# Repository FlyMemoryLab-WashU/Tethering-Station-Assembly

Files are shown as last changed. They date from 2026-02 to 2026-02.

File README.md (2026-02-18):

# Instructions for building the inexpensive tethering station
---
<div align="center">
  
    <p><strong>Figure 1:</strong> Fly tethering station.</p>
</div>

### Table of Contents
- [1. Prepare all needed parts](#1-prepare-all-needed-parts)
- [2. Assemble the acrylic frame](#2-assemble-the-acrylic-frame)
- [3. Assemble the peltier cooler](#3-assemble-the-peltier-cooler)
- [4. Mount the micromanipulator](#4-mount-the-micromanipulator)
- [5. Install the thread adapter and Mini-V clamp](#5-install-the-thread-adapter-and-mini-v-clamp)
- [6. Install the fly-holding rod and fly holder](#6-install-the-fly-holding-rod-and-fly-holder)
- [7. Power on and set the cooler temperature](#7-power-on-and-set-the-cooler-temperature)
- [8. Required parts list](#8-required-parts-list)
  
## Assembly Steps

### 1 Prepare all needed parts

#### 1.1 Verify purchasable items
- Confirm you have all **purchasable components** listed in the **Required Parts List (PPL)** table.
- Purchase any missing items before starting the build.

#### 1.2 Prepare custom acrylic parts
- You need to prepare:
  - a. Acrylic fly holder.
   <div align="center">
    
    <p><strong>Figure 2:</strong> Acrylic fly mount, 1.5mm (1/16”) thickness.</p>
    </div>
    
  - b. Acrylic assembly for the tethering station.
    <div align="center">
        
    <p><strong>Figure 3:</strong> CAD rendering of the tethering station's acrylic assembly, designed in FreeCAD.</p>
    </div>
  
- Obtain these acrylic-sheet parts by either:
  - Laser-cutting the acrylic sheets yourself, or
  - Ordering laser-cut parts from a service (e.g., Ponoko).
- Check acrylic thickness before cutting/ordering. The SVG filenames indicate the required thickness:
  - **1.5 mm (1/16")**
  - **6 mm (1/4")**
- Cut paths only: all paths in the SVG files are intended to be **cut**, not engraved.
  - [Download fly holder SVG files](Fly_holder_1point5mm.zip)
  - [Download tethering station SVG files](Tethering-Station-v3.2.zip)
      
#### 1.3 Tap threads in the baseplate
- Tap **M3 threads** into the baseplate holes used to mount the micromanipulator.

#### 1.4 Prepare 3D-printed parts
- Obtain the 3D-printed parts by either:
  - Printing them yourself, or
  - Ordering them from a service (e.g., Craftcloud).
- Recommended filament:
  - **PLA** (works well for most uses)
  - **ASA** (recommended if you need improved UV resistance)
- Suggested print settings:
  - **0.2 mm layer height**
  - **No supports**
- Mini-V clamp: insert **M3 nuts** into both slots.

---

### 2 Assemble the acrylic frame
- Assemble the main structure using the acrylic parts, following the render in **Figure 3**.
- Fasten all acrylic joints with **cyanoacrylate adhesive** (super glue), as shown in **Figure 3**.

#### Optional: add rubber feet
For a better grip between the baseplate and the table, attach **four rubber feet** under the baseplate—**one at each corner**.

---

### 3 Assemble the peltier cooler

#### 3.1 W1209 temperature controller    
-   <div align="center">
       
    <p><strong>Figure 4:</strong> HiLetgo 2pcs W1209 with Case 12V DC Digital Temperature Controller.</p>
    </div>
    
- Assemble the **W1209 temperature controller (PPL)**.
- If your unit includes an acrylic housing, assemble the housing first.

> **Wiring safety note**
>
> Do **not** splice wires by twisting metal-on-metal only. Poor splices can overheat under load.
> Use one of the following:
> - solder + heat-shrink, or
> - proper connectors (e.g., crimp connectors or WAGO lever nuts).

#### 3.2 Wire the temperature controller to the peltier cooler
Prepare:
- one **3" red wire** (cut + strip ends)
- one **10" black wire** (cut + strip ends)
- **12 V power supply**
- **female barrel connector**
- **rocker switch**
- **Peltier cooloer**    
    <div align="center">
    
    <p><strong>Figure 5:</strong> Thermoelectric, Peltier Assemblies.</p>
    </div>

Wire as follows:
a. Use the **3" red wire** to connect terminals **K1 → 12V** on the W1209.
b. Connect one end of the **10" black wire** to **GND** on the W1209.
c. Connect the other end of the **10" black wire** to the **negative (−)** terminal of the **female barrel connector**.
d. Connect the **black wire** of the **rocker switch** to **12V** on the W1209.
e. Connect the **red wire** of the **rocker switch** to the **positive (+)** terminal of the **female barrel connector**.

**Cooler load wiring (Peltier + fan assembly):**
- **Red wires → K0**
- **Black wires → GND**

You can wire the cooler load either **now** or **after** mounting the cooler to the acrylic structure.

#### 3.3 Prepare and mount the aluminum T-bar
a. Cut a **40-mm-length** piece of the **aluminum T-bar** (a bandsaw works well).
b. Apply **thermal paste** to the bottom face of the T-bar (orientation as in **Figure 1**).
c. Place the **NTC temperature probe** so it touches **both**:
   - the rim of the T-bar, and
   - the cold plate  
   Add thermal paste to thermally couple the probe to both surfaces.
d. Secure the T-bar using **thermal tape** (use **4 × 10 mm** strips) as shown in **Figure 6**.
   
   - You do **not** need to remove the blue liner from the tape after applying it.

-   <div align="center">
    
    <p><strong>Figure 6:</strong> The aluminum T-bar on the cooler</p>
    </div>

#### 3.4 Seat the cooler on the acrylic frame
- Place the cooler into its seat as shown in **Figure 1**.
- Optionally use **cyanoacrylate adhesive** (super glue) for additional fastening.

---

### 4 Mount the micromanipulator
a. Place the micromanipulator on the acrylic baseplate **with the 6 mm raising platform underneath**.
b. To access the screw mounts:
   - Slide the lowest platform to an **edge position** to expose the screw holes on the opposite side.
c. Insert **M3 × 12** screws and fasten the micromanipulator into the baseplate.
d. Move the platform to the other edge position and repeat to install the remaining screws.

---

### 5 Install the thread adapter and Mini-V clamp

a. Screw your chosen **thread adapter** into the top surface of the micromanipulator.
b. Wrap **one layer** of **PTFE (thread seal) tape** or **electrical tape** around the exposed threads to add friction (prevents the clamp from rotating freely).
c. Attach the **Mini-V clamp** above the thread adapter.

#### Notes by clamp version

**3D-printed version (shown in Figure 1)**
- The “thread adapter” is an **M3 × 36** threaded rod.
  - We made this by cutting an **M3 × 40** screw down to **36 mm** using a rotary tool + cutoff wheel (other methods are fine).
- Fasten the rod by:
  a. threading it into the micromanipulator platform hole closest to the T-bar, then
  b. adding a **washer + nut** to lock it in place.

**Thorlabs-parts version**
- You may need **M3 standoffs** to reach the height of the aluminum T-bar apex.
- This was not tested; an M3 standoff kit is included in the PPL as an option.

---

### 6 Install the fly-holding rod and fly holder
a. Insert the appropriate **thumb screw** into the top of the Mini-V clamp (type depends on your clamp choice).
b. Insert the **fly-holding rod** (Thorlabs or 3D-printed) into the Mini-V clamp and secure it with the thumb screw.
c. Attach the acrylic fly holder to the rod using one of the following:
   - **M2.5 screw + nut**, or
   - **#2-56 screw + nut**
d. Use the small hole at one end of the fly-holding rod for the fly holder fastener.

---

### 7 Power on and set the cooler temperature

a. Plug the **12 V power supply** into the **female barrel connector**.
b. Turn on the **rocker switch** when you are ready to cool.

#### Recommended temperature setpoint
- Target: keep the **cold plate ~0 °C**.
- The NTC probe may not report the cold-plate temperature accurately.
- Using an IR camera, we found that setting the controller to **+10 °C** produced the desired cold-plate temperature (~0 °C).

#### How to set the temperature on the W1209
a. **Click** (do not long-press) the **SET** button, which will make the display flash.
b. Use **+** and **−** to adjust the set temperature.
c. Click the SET button again to set the displayed temperature.

## 8 Required parts list

| Name | Quantity | Description | Notes | Link |
|------|----------|-------------|-------|------|
| Tap Wrench Tool Set | 1 | Mesee 6 Pcs Tap Wrench Tool Set, Adjustable T-Handle Tap Holder Wrench with Metric Plug Taps (M3–M8) | | [Amazon](https://a.co/d/hpTYyof) |
| Super Glue | 1 | Loctite Super Glue Professional Liquid, 20 g | | [Amazon](https://a.co/d/eSluuwc) |
| Temperature Controller | 1 | HiLetgo W1209 (12V) Digital Temperature Controller (with case) | | [Amazon](https://a.co/d/bQPwmGg) |
| WAGO Lever Splice | 5 | Push-in butt splice connector, 12–24 AWG, transparent/orange | | [DigiKey](https://www.digikey.com/short/qq5hc085) |
| Black Wire | 1 | 22 AWG hook-up wire, black, 25 ft (7.62 m) | | [DigiKey](https://www.digikey.com/short/qm3t1whb) |
| Red Wire | 1 | 22 AWG hook-up wire, red, 25 ft (7.62 m) | | [DigiKey](https://www.digikey.com/short/whnmh5cv) |
| Rocker Switch | 1 | Rocker switch, SPST, 20A (AC) 125V, panel mount, snap-in | | [DigiKey](https://www.digikey.com/short/8pzjtrjv) |
| Thermal Tape | 1 | Double-sided thermal adhesive tape, 25 m × 10 mm × 0.20 mm | | [Amazon](https://a.co/d/jgPTIG2) |
| Thermal Paste | 1 | Thermal silicone compound, 1 g syringe | | [DigiKey](https://www.digikey.com/short/015wb8zm) |
| Cooler | 1 | Direct-to-air thermoelectric assembly | | [DigiKey](https://www.digikey.com/short/zvf0w91p) |
| Power Supply | 1 | 12V 8A (96W) AC/DC power adapter | | [Amazon](https://a.co/d/hwq6SQs) |
| Micro-Manipulator | 1 | XYZ axis manual precision linear stage (40 × 40 mm) | | [Amazon](https://a.co/d/8RHpoLn) |
| Bumper Feet | 4 | Square tapered bumper feet (polyurethane) | Optional; example part | [DigiKey](https://www.digikey.com/short/tmd9vchq) |
| Aluminum T-Bar | 1 | 6061 aluminum T-bar, 1/2" high × 1" wide, 1/8" wall | Buy 2 ft; cut a 40 mm section (bandsaw) | [McMaster](https://www.mcmaster.com/1668T72-1668T722/) |
| Plate-Holding Rod (Thorlabs option) | 1 | ER90C - 90° "T" Extension | Or 3D print | [Thorlabs](https://www.thorlabs.com/thorproduct.cfm?partnumber=ER90C) |
| Cage Rod (for plate-holding rod) | 1 | ER2 - Cage Assembly Rod, 2" long, Ø6 mm | Used with ER90C | [Thorlabs](https://www.thorlabs.com/thorproduct.cfm?partnumber=ER2) |
| Electrical Tape (McMaster) | 1 | Electrical tape, 3/4" wide, 60 ft, black | | [McMaster](https://www.mcmaster.com/7619A11/) |
| Electrical Tape (DigiKey) | 1 | Electrical tape, PSA adhesive, black, 3/4" × 60' | Alternative source | [DigiKey](https://www.digikey.com/short/hzwqm2b5) |
| PTFE Seal Tape | 1 | PTFE thread seal tape (plumber's tape), 1/2" × 520" | | [Amazon](https://a.co/d/2TIa52S) |

## Clamp Options

### Option A: Imperial (8-32)

| Name | Quantity | Description | Notes | Link |
|------|----------|-------------|-------|------|
| Thumb Screw | 1 | #8-32 hex head thumb screw, hex drive, nylon | | [DigiKey](https://www.digikey.com/short/10z84wm7) |
| Thread Adapter | 1 | Male hex thread adapter, 8-32 to M3 × 0.5 | | [McMaster](https://www.mcmaster.com/91091A527/) |
| Clamp | 1 | VH1 - Miniature V-Clamp, 0.42" long, 8-32 tapped | | [Thorlabs](https://www.thorlabs.com/thorproduct.cfm?partnumber=VH1) |
| M3 Standoff Kit | 1 | M3 standoff assortment kit | Optional height tuning | [Amazon](https://a.co/d/eljB6fC) |

### Option B: Metric (M4)

| Name | Quantity | Description | Notes | Link |
|------|----------|-------------|-------|------|
| Thumb Screw | 1 | #8-32 hex head thumb screw, hex drive, nylon | | [DigiKey](https://www.digikey.com/short/10z84wm7) |
| Thread Adapter | 1 | Male hex thread adapter, M3 × 0.5 to M4 × 0.7 | | [McMaster](https://www.mcmaster.com/93047A106/) |
| Clamp | 1 | VH1/M - Miniature V-Clamp, 0.42" long, M4 tapped | | [Thorlabs](https://www.thorlabs.com/thorproduct.cfm?partnumber=VH1/M) |
| M3 Standoff Kit | 1 | M3 standoff assortment kit | Optional height tuning | [Amazon](https://a.co/d/eljB6fC) |

### Option C: Metric (3D-printed clamp)

| Name | Quantity | Description | Notes | Link |
|------|----------|-------------|-------|------|
| Thumb Screw | 1 | Knurled thumb screws, M3 × 20 | | [Amazon](https://a.co/d/elruBuP) |
| Thread Adapter | 1 | M3 × 36 threaded rod | Fabricate per procedure (e.g., cut down an M3 × 40) | |

## Fasteners

| Name | Quantity | Description | Notes | Link |
|------|----------|-------------|-------|------|
| Screws (M3 × 12 mm) | 1 | 316 stainless button head hex drive screws, M3 × 0.5, 12 mm | | [McMaster](https://www.mcmaster.com/94500A264/) |
| Nuts (M3) | 1 | Zinc-plated steel hex nut, M3 × 0.5 | | [McMaster](https://www.mcmaster.com/90591A121/) |
| Washers (M3) | 1 | 18-8 stainless washer for M3 (3.2 mm ID, 7 mm OD) | | [McMaster](https://www.mcmaster.com/93475A210/) |
| M3 Fastener Kit | 1 | M3 screw/nut/washer assortment kit | Alternative to individual parts | [Amazon](https://a.co/d/aGirgUi) |
| Screw (#2-56) | 1 | #2-56 pan head slotted drive nylon screw | For acrylic fly holder fastening | [DigiKey](https://www.digikey.com/short/0jq8jp8r) |
| Nut (#2-56) | 1 | #2-56 hex nut, nylon | For acrylic fly holder fastening | [DigiKey](https://www.digikey.com/short/2qt794vw) |

## Acrylic Sheets (if cutting in-house with a CO₂ laser)

| Name | Quantity | Description | Notes | Link |
|------|----------|-------------|-------|------|
| Acrylic sheet (1/16", 1.5 mm) | 1 | Clear scratch- and UV-resistant acrylic sheet, 12" × 12" × 1/16" | For 1.5 mm SVG parts | [McMaster](https://www.mcmaster.com/8589K11/) |
| Acrylic sheet (1/4", 6 mm) | 1 | Clear scratch- and UV-resistant acrylic sheet, 12" × 12" × 1/4" | For 6 mm SVG parts | [McMaster](https://www.mcmaster.com/8589K81/) |

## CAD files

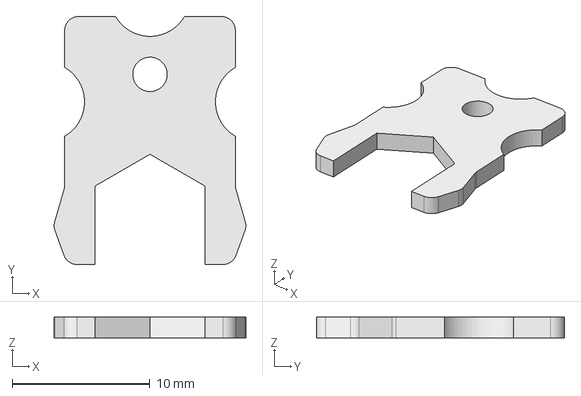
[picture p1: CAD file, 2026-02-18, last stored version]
lasercut_1point5mm.FCStd
13.9 x 18.0 x 1.50 mm

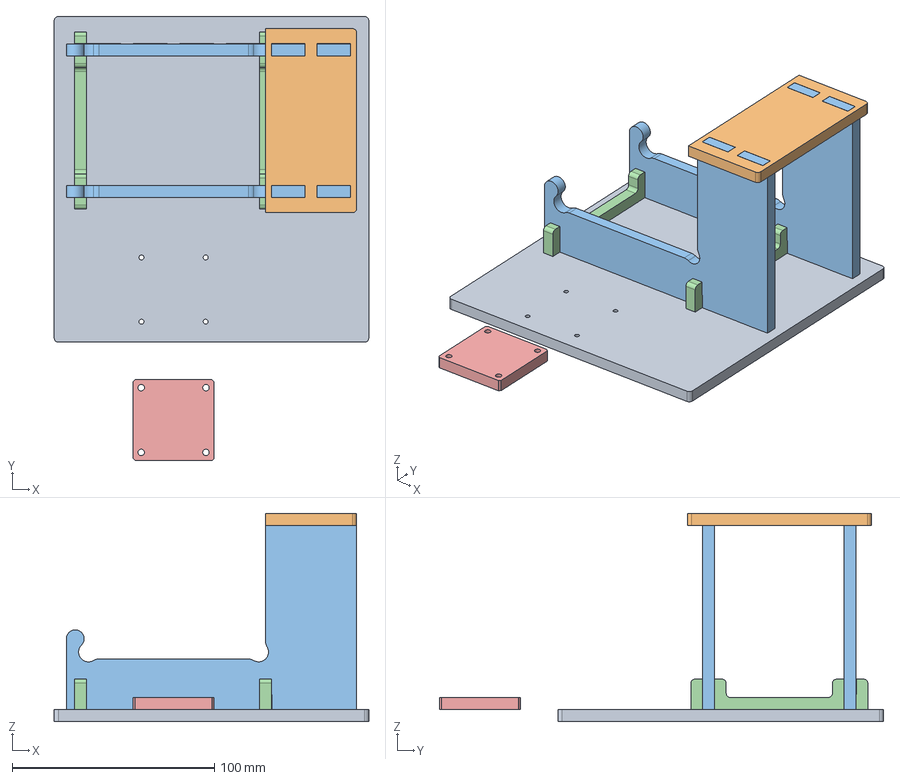
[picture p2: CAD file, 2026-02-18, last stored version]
Tethering-Station-v3.2.FCStd
155.5 x 219.5 x 103.0 mm
Base
Top
Left x 2
Far x 2
Raise

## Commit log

2026-02-06 Revise README for tethering station assembly instructions
    Updated the README to reflect changes in the project name and improved instructions for assembling parts.
2026-02-06 Revise acrylic assembly instructions and add optional step
    Updated assembly instructions for clarity and added optional step for rubber feet.
2026-02-06 Revise assembly steps and improve formatting
    Updated assembly instructions and section headings in README.
2026-02-06 Revise table of contents for assembly instructions
2026-02-06 Revise parts list and add clamp options
    Updated the required parts list to include new components and their details. Added clamp options and fasteners sections with descriptions and links.
2026-02-13 Refactor README for improved clarity and structure
    Updated formatting and structure of the README file, including section headings, table of contents, and assembly steps.
2026-02-13 Revise README for clarity and formatting improvements
    Updated README formatting and improved clarity of assembly instructions, including sections on parts and assembly steps.
2026-02-13 Refactor README for better formatting and clarity
    Updated formatting for images and figures in the README. Improved clarity in instructions for preparing acrylic and 3D-printed parts.
2026-02-13 Update README for peltier cooler assembly steps
2026-02-17 Add image and description for Peltier assemblies
2026-02-17 Add images for W1209 temperature controller
    Added images for W1209 temperature controller in the README.
2026-02-17 Remove image from README for W1209 controller
    Removed an image from the W1209 temperature controller section.
2026-02-17 Fix formatting in temperature controller section
